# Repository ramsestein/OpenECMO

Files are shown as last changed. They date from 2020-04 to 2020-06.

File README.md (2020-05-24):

# ECMO

*Extra Corporeal Membrane Oxygenation* 

> *Nota:* Este documento se actualiza continuamente a medida que evoluciona el proyecto, por favor, revísalo frecuentemente y si crees que falta algo solicita que lo actualicemos.

## ¿Qué es una ECMO? ##
Una **ECMO** o **Membrana de Oxigenación Extra Corpórea** es una asistencia mecánica circulatoria y respiratoria, capaz de proporcionar soporte cardíaco y pulmonar, durante un periodo de días o semanas, para la insuficiencia cardiaca o respiratoria refractarias a tratamiento convencional. Es en resumen un soporte vital extracorpóreo con oxigenador incorporado. 

> A diferencia de los sistemas de perfusión o bypass cardio-pulmonar que están diseñados para sustituir de forma completa y breve la función del corazón y pulmón en el quirófano y así facilitar la cirugía, la **ECMO** mantiene la asistencia necesaria para garantizar las funciones vitales durante un periodo de tiempo mayor.

Este artículo de la _Revista Española de Perfusión_ nos parece muy interesante e ilustrativo para todos aquellos que quieran entender el problema y sería casi de lectura obligatoria si realmente quieres ayudar: [Soporte vital extracorpóreo. Oxigenación por
membrana extracorpórea. ECMO](https://www.aep.es/articulo/71/Monogra%CC%81fico%20ECMO.pdf "Soporte vital extracorpóreo. Oxigenación por
membrana extracorpórea. ECMO")

El dispositivo que queremos crear es del tipo ECMO V-V (Venoso-Venoso), que plantea menos problemas de presión sanguínea que el V-A (Venoso-Arteria)

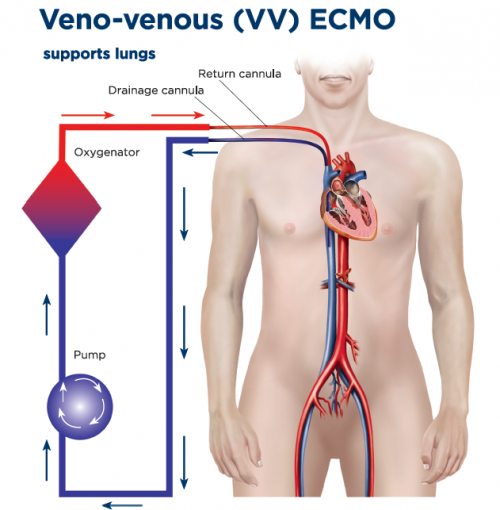
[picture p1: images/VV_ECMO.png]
ECMO Venoso-Venoso


## ¿Por qué un ECMO?

**El problema**
Además de la falta de respiradores hay otra crisis que inicialmente se pasó por alto: 
https://www.infobae.com/america/the-new-york-times/2020/04/19/coronavirus-ademas-de-la-falta-de-respiradores-hay-otra-crisis-que-se-paso-por-alto/

**¿Qué se puede hacer?**
Ramsés Marrero convova en el foro A.I.R.E. https://foro.coronavirusmakers.org/index.php?p=/discussion/comment/2749 este proyecto de clase 3.

## El proyecto ##
Intentamos construir una ECMO maker que cumpla con parámetros hemodinámicos suficientes para mantener con vida a pacientes muy graves afecados por COVID-19. 

> Recuerda que se trata de emular el comportamiento de un dispositivo comercial pero queremos construir algo low-cost pero con garantías médicas.

> *Nota importante:* Todos los que se acaben de añadir al proyecto les recomedamos la visualización del siguiente **[vídeo](https://gitlab.com/coronavirusmakers/ecmo/-/raw/master/files/zoom_Ramses.mp4?inline=true "Ramsés explica en que consiste un ECMO")** de una videoconferencia en la que el médico Ramsés Marrero explica de que se trata.
También rogamos encarecidamente que lean toda la información disponible antes de preguntar por los grupos de Telegram cuestiones que ya están resueltas.

Los objetivos hemodinámicos que debemos intentar conseguir tras la colocación del ECMO son:
* Flujo inicial del ECMO 50 – 80 ml/Kg./min. 
* Presión arterial media ≥ 65 mmHg. 
* Índice cardiaco ≥ 2.5 l/min./m2. 
* Presión de enclavamiento de arteria pulmonar (PEAP) 8-14 mmHg
* PVC 8-10 mmHg. 
* Saturación venosa mixta >65%. 
* Restauración de la diuresis (>0,5 ml/Kg. /h.) 
* Disminuir el ácido láctico en las primeras 4 horas.

## Esquema inicial ##

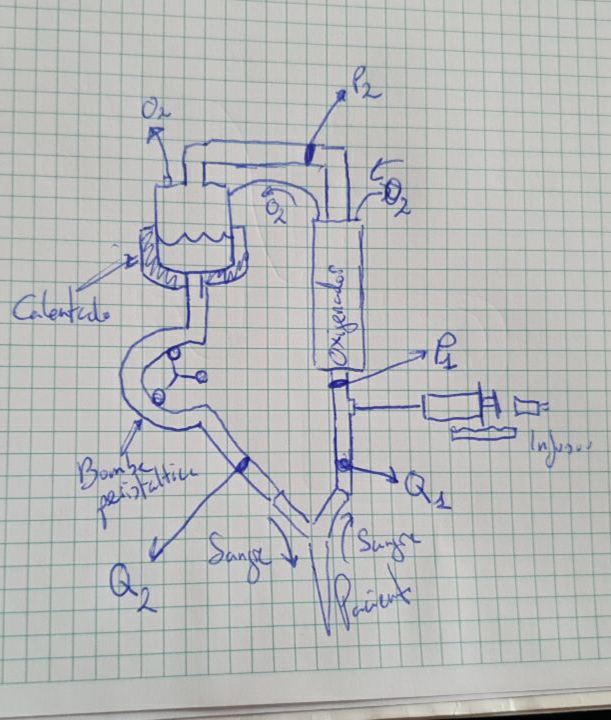
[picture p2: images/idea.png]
Idea Ramsés explica en que consiste un ECMO


*Presiones intrasistema:*
* P1: presión negativa de succión venosa (valores normales hasta -70 mmHg)
* P2: presión entre la bomba y el oxigenador (valor máximo de la normalidad entre   250 - 300 mmHg).
* P3: presión entre el oxigenador y la cánula arterial (valor máximo de la normalidad entre 250 – 300 mmHg).
* Diferencial de presión (calculado) ∆P (P2 – P3)

## Componentes del sistema ##

### Consola ###
* Es la encargada del control hemodinámico del sistema.
* Permite regular la velocidad de rotación de la bomba peristáltica (RPM) y el flujo en litros por minuto (LPM)
* Muestra la información aportada por los sensores hemodinámicos, bioquímicos o de seguridad implantados en el circuito.

### Bomba peristáltica ###
* Se necesita lograr un caudal de hasta 6 Litros por minuto (Lpm).
* Se descarta el uso de una bomba centrífuga porque tendría que ser de grado médico aunque es la que se usa en sistemas comerciales modernos.

### Tubos ###
* El tubo interior que aplasta debe tener un diámetro de 7mm externo y 6mm de diámetro interno para aprovechar los que hay de forma abundante en los hospitales.
* Para conseguir suficiente caudal (de hasta 6Lpm) se ha determinado que serán necesarios al menos dos tubos de ese diámetro.
* Los tubos no tienen porque ser de grado médico, podrían valer tubos de acuario suficientemente blando para poder aplastarse en la bomba peristáltica (* para los prototipos)

### Sensores ###

Algunas ideas:
* Interesa conocer la presión antes y después del filtro y también al final del recorrido
* De nuevo la presión hay que medirla de forma indirecta (sin “tocar” la sangre) o utilizar sensores desechables.

* Presión:
    * Dendrómetro
    * Webcam + machine learnnig para ver el flujo
    * Ultrasonidos / Doppler
    * Sensores barométricos / de presión
    * Detectar el desplazamiento de una jeringuilla de baja presión
    
* Para detectar obstruccion:
    * Utilización de un oxímetro
    * Medida de la corriente del motor o uso de sensores hall para determinar si la velocidad de giro es la prefijada.

### Oxigenador ###
Es el elemento esencial del EMCO, la membrana que permite la oxigenación de la sangre del paciente. 
* Opción de usar un modelo comercial.
* Se están estudiando tamnbién distintas opciones de fabricación 

### Perfusor ###
Es un elemento adicional (independiente) que permite la infusión de heparina para evitar la coagulación de la sangre.

## Colaboración ##

Si crees que puedes ayudar entra en los grupos de Telegram y dirígete al subgrupo en el que creas que puedes aportar más: 
https://t.me/joinchat/AEZqrlHdWOAwDOvL7WSOKA

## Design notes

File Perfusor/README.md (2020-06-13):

# Perfusor #

## Descripción ##
La bomba de perfusion (o infusión) es un dispositivo que dispensa fluido durante un período de tiempo determinado. 

Info de la wikipedia: https://es.wikipedia.org/wiki/Bomba_de_infusi%C3%B3n

## Proyecto ##
* El diseño mecánico se basa en un diseño de actuador lineal junto a una jeringa, controlado por un sistema electrónico.
* El dispositivo debe ser independiente del resto del sistema [ECMO](https://gitlab.com/coronavirusmakers/ecmo "ECMO").
* La jeringa se coloca en el perfusor ya purgada.

El diseño usara una jeringa 50-60 ml tipo BD Plastic o similar (diametro 26.7 mm) 

[Jeringuilla](https://gitlab.com/coronavirusmakers/ecmo/-/raw/master/images/jeringuilla.jpeg "Jeringuilla de 50-60ml")

[Datos y tamaños de las jeringuillas](https://gitlab.com/coronavirusmakers/ecmo/-/raw/master/files/Syringe-Selection-Guide.pdf "Datos de las jeringuillas")

## Requerimientos funcionales ##
* Tenemos que lograr un control entre 0.1ml/h - 1200ml/h para una jeringuilla de 50ml (valores calculados)
* Resolución de 0.1 mL
* Dosis tipica es de 2-15ml/h
* Velocidad ajustable
* Posibilidad de hacer una embolada puntual de x mL
* Indicación de estado
* indicador de alarma cuando este al 95% del final
*  La interface de usuario debe permitir:
    * Indicar y modificar la velocidad de perfusion
    * Cargar nueva jeringa (volver al inicio de carrera)

## Hardware ##

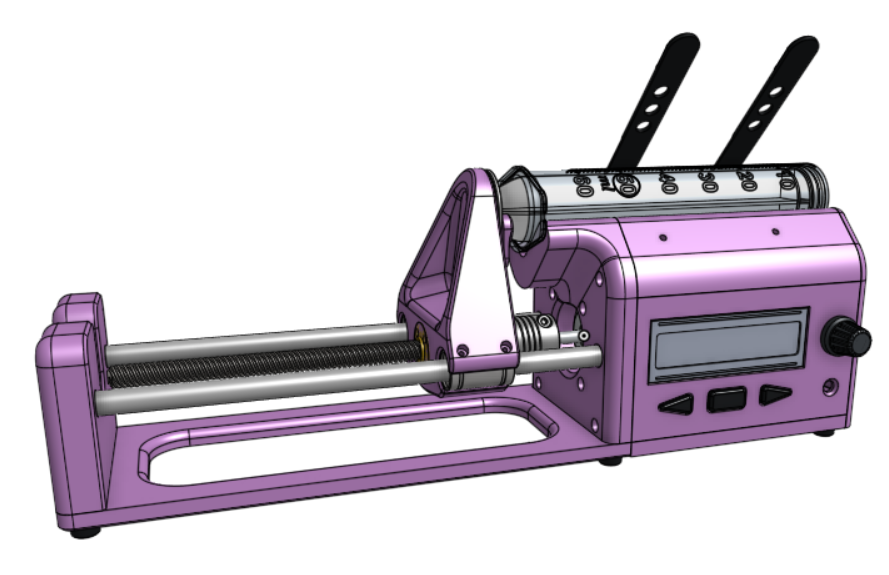
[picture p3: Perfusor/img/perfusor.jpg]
Montaje del perfusor


### Mecánica ###

El sitema mecánico consta de:
* Piezas impresas en 3D
* Motor paso a paso nema 17
* Un sistema de husillo / cremallera.. (por concretar)
* 2 Rodamientos LM8UU
* Tornillos M3

### Electrónica ###
El sitema electrónico consta de:
* 1 Fuente de alimentación de 12V
* 1 Conversor DC-DC
* 1 microcontrolador tipo Arduino o un microprocesador similar
*  Motor diver supported by [AccelStepper](https://www.airspayce.com/mikem/arduino/AccelStepper/index.html)
* 1 sensor final de carrera o endstop (mejor óptico o hall para evitar problemas de pérdida de pasos pero también pueden ser mecánicos)
* Display (Pantalla LCD I2C 16x2, 20x4 u OLED)
* Tres botones
* Codificador rotatorio (encoder para selección de opciones) o un potenciómetro
* LEDs indicadores de estado (Verde: Operativo; Rojo: Alarma)
* Alarma sonora (zumbador) 

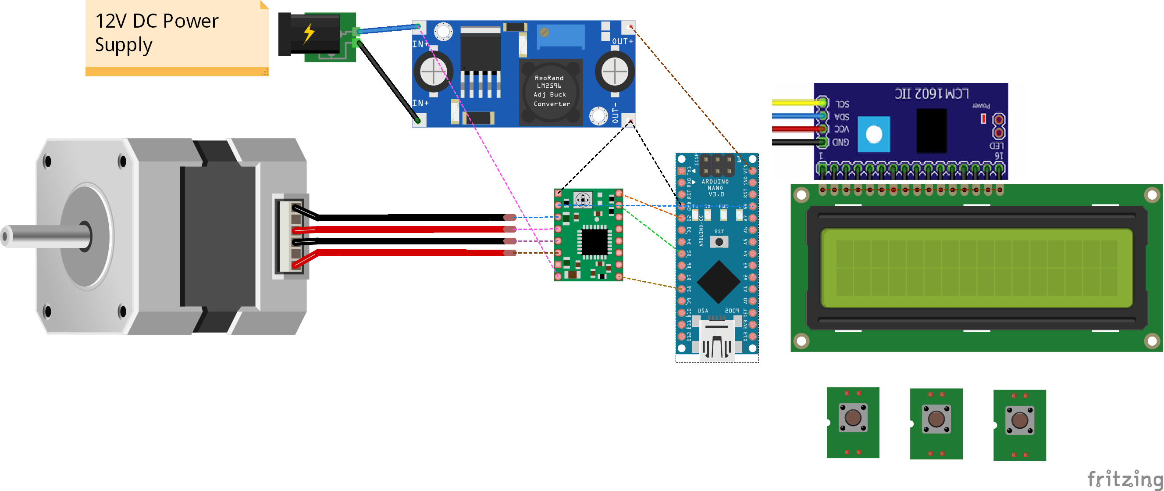
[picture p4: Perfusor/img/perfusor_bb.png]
Esquema del perfusor

(Este esquema está incompleto pero sirve como referencia)
## Diseño actual (en desarollo) ##

https://cad.onshape.com/documents/83fc61005005f6cafa1e611e/w/66630729656df7a5a0b484c3/e/114f94c28aaf946ab67668a8

En la carpeta stl hay unos archivos en formato .stl para la  impresión en 3D de la estructura del dispositivo.

https://gitlab.com/coronavirusmakers/ecmo/-/tree/master/Perfusor/stl 

En la carpeta stl/Plastikete hay una versión low-cost completamente de plástico

https://gitlab.com/coronavirusmakers/ecmo/-/tree/master/Perfusor/stl/Plastikete 

## Como testear el perfusor

## Enlaces de interes ##
### Diseños ###
1. http://biohackacademy.github.io/biofactory/class/8-pumps/
2. https://github.com/gniezen/openpump
3. https://docs.google.com/document/d/1zW16lL-d0ZAO8lZd7ANE9CllARVIuFvh3bQfag9HGlk/mobilebasic#

### Cálculos ###

    * Aquí tenemos un enlace con cálculos al respecto de los husillos: https://docs.google.com/spreadsheets/d/1-_jbQUJL_gpxpd1H1qJIKm36sRTwBJtxHg9JuVWixjs/edit#gid=0

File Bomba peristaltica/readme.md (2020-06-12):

# Bomba Peristáltica  #

## Descripción ##
Una bomba peristáltica es un tipo de bomba hidráulica de desplazamiento positivo usada para bombear una variedad de fluidos.
Nosotros queremos construir una bomba peristáltica para impulsar la sangre a través de un sistema venoso-venoso de un ECMO.

En el siguiente enlace https://ocw.unican.es/mod/page/view.php?id=537 hay una sencilla pero completa descripción de la hemodinámica o física del flujo sanguíneo.

## Requerimientos funcionales ##
* Bombeo continuo
* Resolución de 1 ml
* Dirección hacia adelante / hacia atrás
* Velocidad ajustable

## Hardware ##

El sitema *mecánico* consta de:
* Motor paso a paso
* Una caja impresa en 3D con rodamientos para hacer la bomba peristáltica 
* Tubos para diálisis de 6mm de diámetro interior y 7mm de diámetro exterior

El sitema *electrónico* consta de:
* Arduino Nano o similar
* Driver para el motor
* Motor paso a paso Nema 23 con eje de 6.35 u 8 mm
* Display (Pantalla LCD I2C 16x2 u OLED)
* Codificador rotatorio (encoder)
* Un botón pera realizar emboladas rápidas. 
* (Quizá un segundo botón)
* LEDs indicadores de estado (Verde: Operativo; Rojo: Alarma)
* Zumbador de alarma

## Diseño actual (en desarollo) ##
Se han subido los archivos de un diseño 3D para motores nema 23 con ejes de 6,23 y 8mm en la carpeta STL que utiliza para probar rodamientos 608zz y otro modelo de bomba peristáltica llamada LEGO.

Estas son algunas imágenes del modelo LEGO:

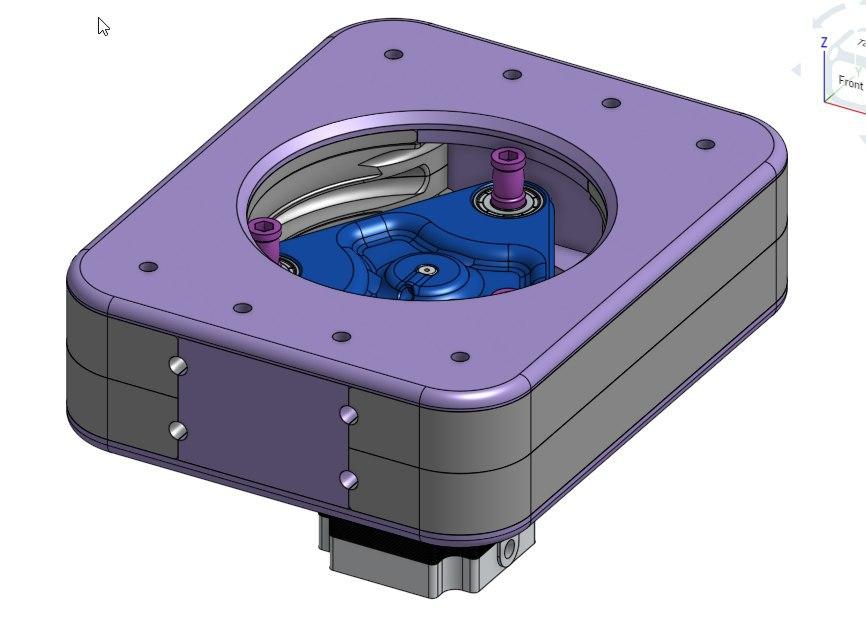
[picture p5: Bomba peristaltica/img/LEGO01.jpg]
LEGO01


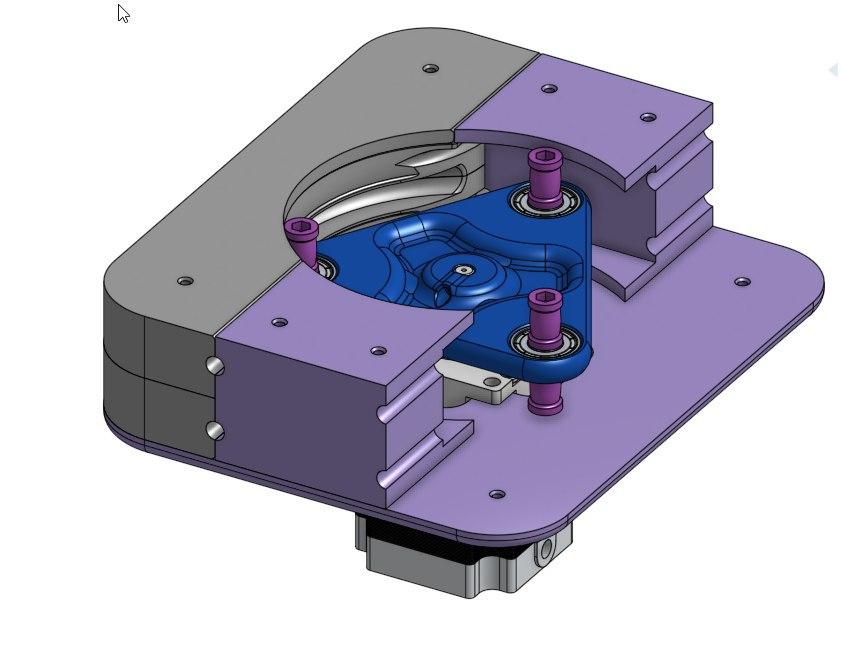
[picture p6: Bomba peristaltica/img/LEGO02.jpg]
LEGO02


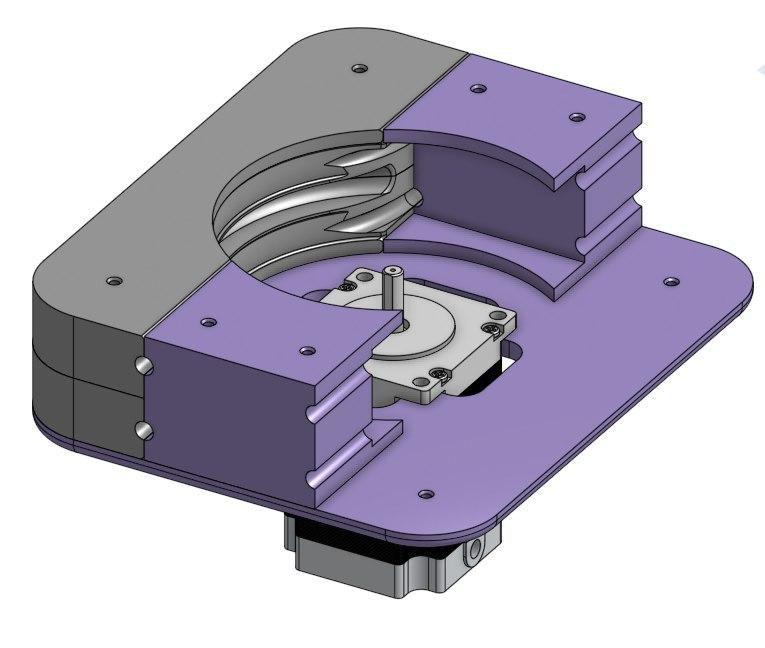
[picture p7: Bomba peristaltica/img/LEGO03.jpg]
LEGO03


Deben utilizarse tubos de 7mm de diámetros exterior y 6mm de diámetro exterior habituales en los hospitales y que se utilizan para diálisis.

## Como testear el bomba persitaltica
* Medición de consumo de corriente
* Encoder
* Sensor hall 

## Enlaces de interes ##
### Diseños ###
1. http://biohackacademy.github.io/biofactory/class/8-pumps/
2. http://2017.igem.org/Team:Aachen/Hardware

### Cálculos ###
1. https://leadfluid.com/how-to-calculate-the-flow-rate-of-leadfluid-peristaltic-pump/

### Médico ###
1. https://ocw.unican.es/mod/page/view.php?id=537

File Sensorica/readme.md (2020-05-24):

**Objetivo**

El objetivo del Sistema de sensores es medir la presión/caudal del sistema y la saturación de oxigeno

**Requisitos**

1. No se puede acceder al líquido, es decir, los sensores no pueden estar en contacto con el líquido y ese es el gran problema
2. Sencillo, barato y fácil de construir.

**Técnicas**

Se ha pensado en las siguientes técnicas:

1. Medida de presión dendrométrica, presionando el tubo y ver la resistencia que ofrece
2. Medida de la velocidad del líquido mediante un sistema óptico o ultrasónico.
3. Medida de O2 en sangre mediante sistema óptico (Colorimetria).

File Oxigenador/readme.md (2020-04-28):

# Intercambiador gases

## Descripción

## Tipos

### PMP

### PDMS

## Como testear el intercambiador de gases

Agitador magnetico

Bomba persitaltica

Sensor presión

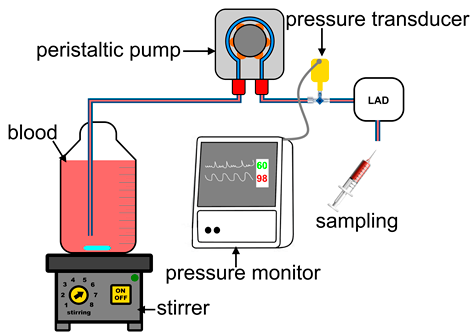
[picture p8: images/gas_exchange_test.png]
Diagrama test intercambiador gas


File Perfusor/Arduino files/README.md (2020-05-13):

# Perfusor
## Overview
The goal is to develop **firmware based on arduino for an syringe driver (infusion pump)**, used to gradually administer small amounts of fluid to a patient, in this case, heparin.
## Hardware Requirements
* Microcontroller: Arduino (any version) or similar 
*  Motor diver supported by [AccelStepper](https://www.airspayce.com/mikem/arduino/AccelStepper/index.html)
* 3 Buttons 
* End stop 
* LCD Display 
* Potentiometer
* Syringe support
* Incremental Encoder(optical+disc)

## How to use it
1. Clone the repository
1. Set up the code in the src/Configuration.h file:
   1. Configure your display
      1. Number of rows
      1. Number of cols
      1. I2C Address of the device
   1. Configure the syringe driver: 
      1. Slider length in mm
      1. Number of steps per turn   
      1. How much it moves per turn
   1. Choose your stepper dirver NEMA17 or BJY. If you want to use any other you have to take into account the interface that it requires and the pins needed.
  *Note: If you are using inverted pins for the driver changes need to be made in the constructor of SyringeDriver (SyringeDriver::SyringeDriver())*
   1. Change the pinout if needed.
1. **Compile and upload the code!**

## Libraries 
* [AccelStepper](https://www.airspayce.com/mikem/arduino/AccelStepper/index.html)
* [NewLiquidCrystal](https://bitbucket.org/fmalpartida/new-liquidcrystal/wiki/Home#!tests)

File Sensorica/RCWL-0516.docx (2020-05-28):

SENSOR DOPPLER MICROONDAS RCWL-0516

1. INTRODUCCIÓN

Para la medida de velocidad de fluidos se ha elegido el módulo RCWL-0516. Este módulo es un interruptor de detección por microondas, que utiliza la frecuencia Doppler de detección. Como utiliza frecuencia Doppler, el circuito no detecta la presencia de un objeto estático delante del sensor, sino el movimiento (velocidad) de un objeto delante del sensor. Al tratarse de un interruptor no es posible utilizar directamente la señal de salida del detector para medir la velocidad.

2. DOCUMENTACION
a) https://www.rogerclark.net/investigating-a-rcwl-9196-rcwl-0516-radar-motion-detector-modules/
b) https://www.tayloredge.com/reference/Electronics/RF/0242.pdf
3. MEDIDA DE VELOCIDAD

Para medir la velocidad de un móvil delante del sensor es preciso acceder a la medida de la frecuencia Doppler. Para ello es preciso extraer la tensión diferencial en la etapa de amplificación del circuito detector (pin 12 del IC RCWL-9196).

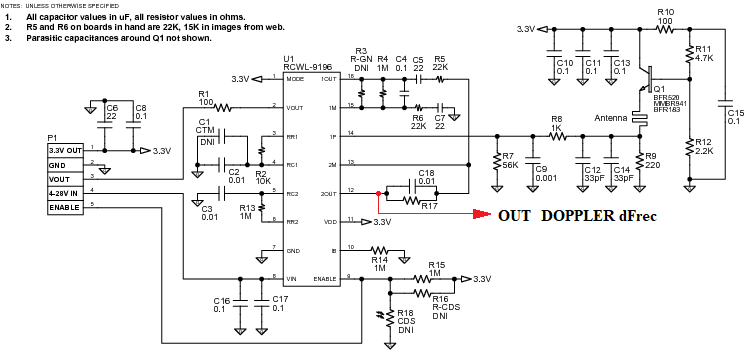
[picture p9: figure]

Fig 1

4. ESTUDIO DEL UMBRAL DE VELOCIDAD DETECTABLE

La señal 2Out del pin 12 del IC RCWL-9196 es una señal analógica cuyo nivel dependerá de la frecuencia de oscilación del circuito resonante conectado en el pin 14 (1C).

VM = Vref * 0.5

Para FDoppler = Frecuencia central tenemos que Vout (2Out) = VM

Si Vref = 5V, luego VM = 2.5V.

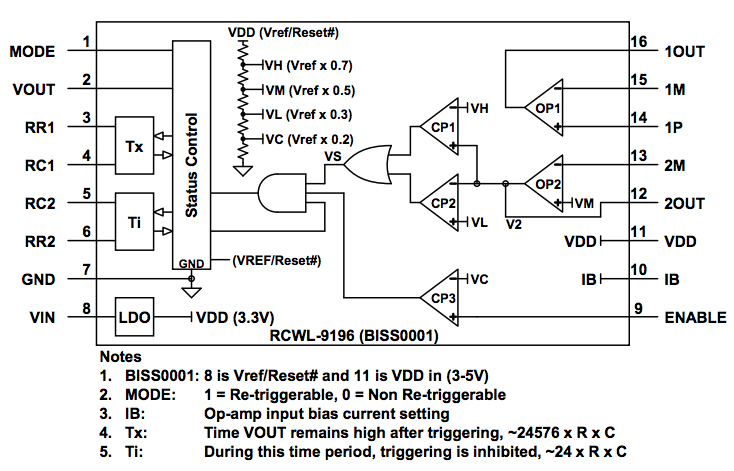
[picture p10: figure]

Fig 2

VL y VH limitan el rango dinámico que para Vref = 5V son VL = 1.5V y VH = 3.5V. El rango dinámico delimita el umbral de la velocidad detectable.

5. APLICABILIDAD A LA MEDIDA DE VELOCIDAD EN UN FLUIDO

La detección de la velocidad de un fluido en movimiento se realiza mediante la medida Doppler sobre las propias moléculas del fluido en movimiento.

6. PRUEBAS CON CORRIENTE DE AGUA

Ejecución de la prueba: Colocando el sensor a 20cm de un grifo abierto el sensor detecta el agua circulando.

Código de prueba:

const int LEDPin = 13;

const int RadarPin = 2;

void setup()

{

pinMode(LEDPin, OUTPUT);

pinMode(RadarPin, INPUT);

pinMode(A0,INPUT);

Serial.begin(9600);

}

void loop()

{

int value= digitalRead(RadarPin);

medida = 0;

if (value == HIGH)

{

digitalWrite(LEDPin, HIGH);

delay(50);

digitalWrite(LEDPin, LOW);

delay(50);

}

else

{

digitalWrite(LEDPin, LOW);

}

}

7. DETECCION DE VELOCIDAD

Para detectar la velocidad de movimiento de un objeto delante del sensor se utiliza el esquema de la figura 1. La tensión en el pin 12 del IC es un valor de tensión analógico entre 0 y Vcc (5V si se conecta a Arduino). Este valor queda limitado a l umbral entre VL y VH. La tensión se acopla a una entrada analógica (A0) del Arduino.

Durante la prueba se comprobado que incluso sin conectar el cable al pin 12 se ha producido inducción en el cable detectando cambios de nivel en función del movimiento delante del sensor.

Código de prueba:

const int LEDPin = 13;

const int RadarPin = 2;

float medida = 0.0;

void setup()

{

pinMode(LEDPin, OUTPUT);

pinMode(RadarPin, INPUT);

pinMode(A0,INPUT);

Serial.begin(9600);

}

void loop()

{

int value= digitalRead(RadarPin);

medida = 0;

if (value == HIGH)

{

digitalWrite(LEDPin, HIGH);

delay(50);

digitalWrite(LEDPin, LOW);

delay(50);

}

else

{

digitalWrite(LEDPin, LOW);

}

for (int i = 0; i <= 100; i++) {

medida = medida + analogRead(Speed);

}

medida = medida / 100;

Serial.println(medida-20);

}

Imágenes:

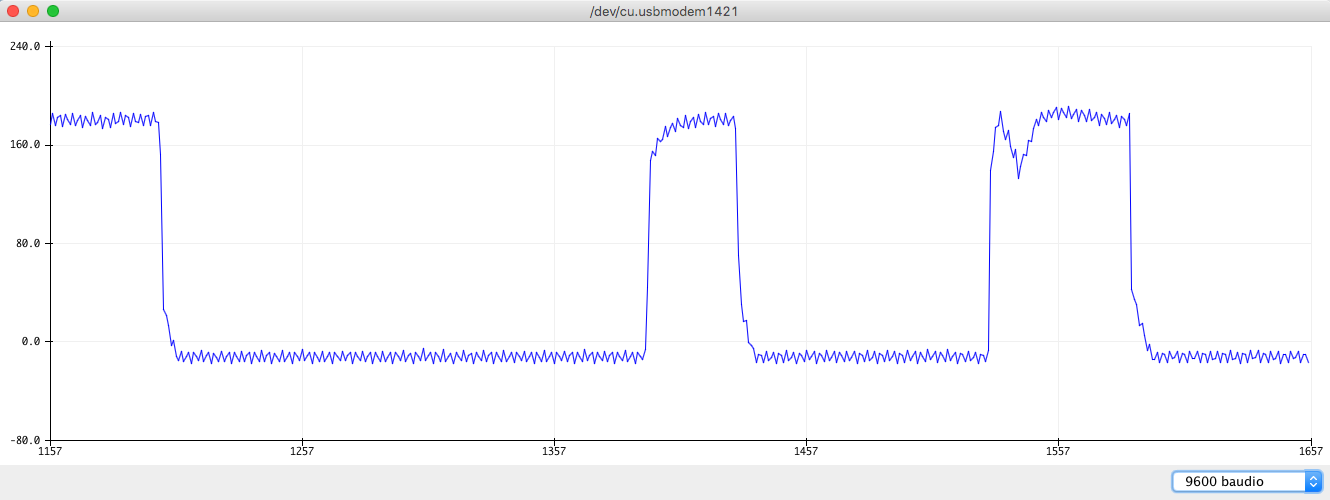
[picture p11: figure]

Fig 3

8. CONCLUSIONES:
- El sensor RCWL-0516 está pensado para la detección de movimiento, no la medida del movimiento.
- Sin embargo, se podría medir el movimiento detectado tomando la tensión del pin descrito.
- La medida de movimiento puede ser ruidosa si no se aisla convenientemente el sensor.

Francisco José Ochando Terreros

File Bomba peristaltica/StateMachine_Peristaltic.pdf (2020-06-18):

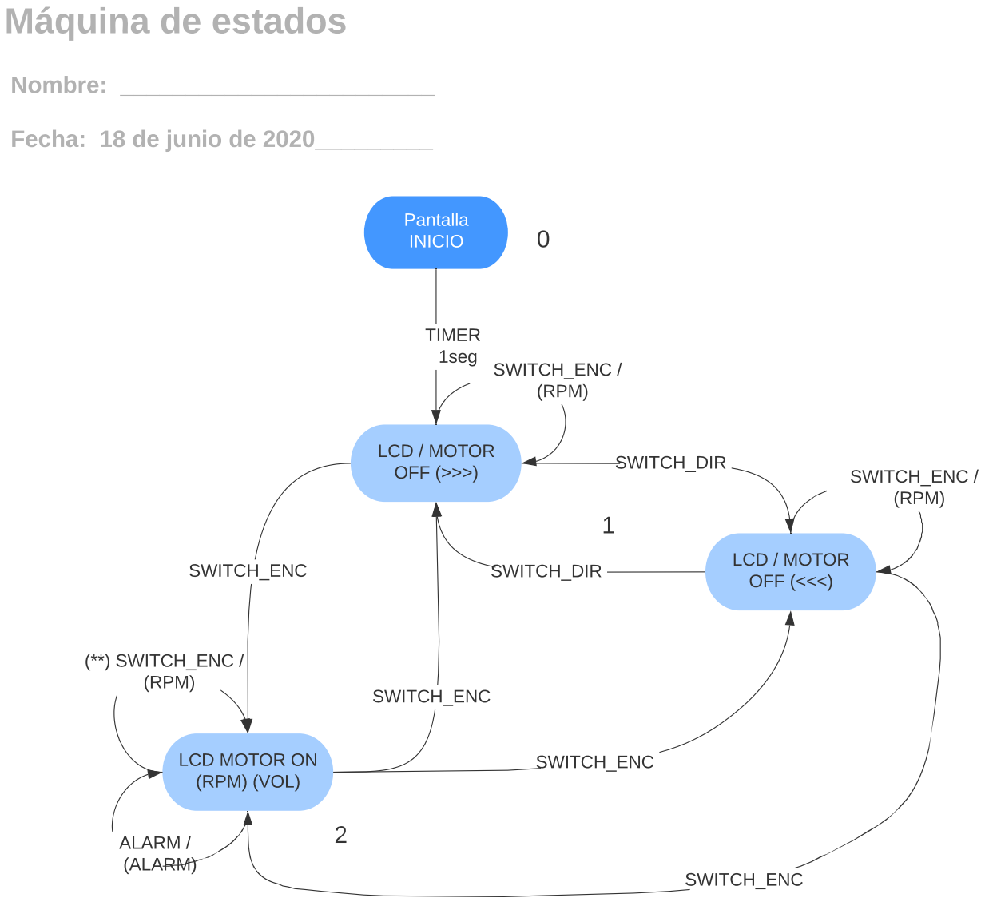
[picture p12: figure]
Pantalla INICIO; LCD MOTOR ON (RPM) (VOL); Máquina de estados; Nombre: ________________________; Fecha: 18 de junio de 2020_________; SWITCH_ENC; LCD / MOTOR OFF (>>>); TIMER 1seg; LCD / MOTOR OFF (<<<); SWITCH_DIR; SWITCH_ENC / (RPM); ALARM / (ALARM); (**) SWITCH_ENC / (RPM)

(0) La Pantalla 0 muestra la información en la pantalla de bienvenida.
(1) La pantalla 1 muestra toda la información (por defecto si no se ha programado una velocidad distinta)
(2) La pantalla 2 muestra toda la información más <ON> y <ALARM> si existe alguna alarma. Motor activado.
(**) El evento mover el potenciometro/encoder rotativo durante el funcionamiento del motor varia los parámetros de giro del motor durante el funcionamiento. Hay que revisar este requisito.

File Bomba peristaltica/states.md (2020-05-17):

# Estados de la máquina

## Documento que describe los estados de la Máquina
En el presente documento se describen los estados de la máquina del LCD en función del estado de los botones, el encoder y los sensores.
El LCD utilizado es un 20x4. La configuración para un LCD 16x2 es posible.
Simulación de LCD en: http://avtanski.net/projects/lcd/

## Estados del LCD en función de los estados de la Máquina
1.	Estado de arranque
Al arrancar la máquina muestra la presentación de bienvenida y las RPM por defecto (configuración de inicio a determinar).

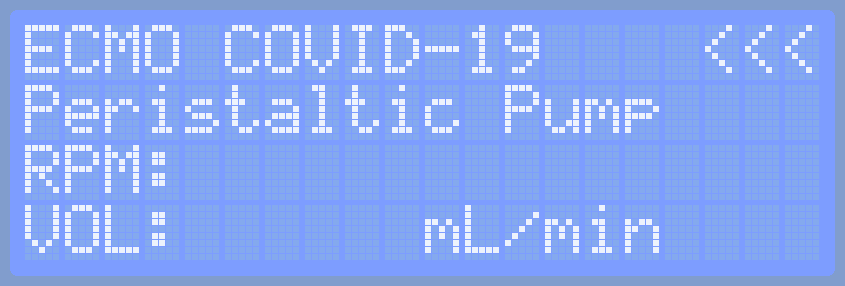
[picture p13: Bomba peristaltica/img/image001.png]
Pantalla inicial del LCD de la bomba peristáltica


2.	Estado de configuración inicio
	Al pulsar el SWITCH_REV se invierte el sentido de la bomba. Esto sólo es posi-ble antes de la marcha del motor o una vez detenido. 

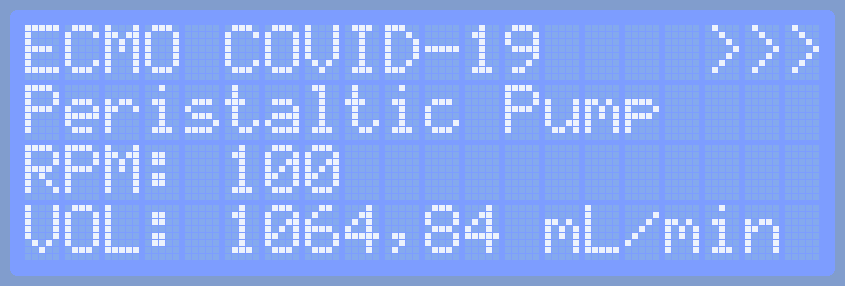
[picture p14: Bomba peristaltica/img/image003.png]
Invirtiendo el sentido de giro


3.	Estado de selección de RPM
	La selección de RPM es posible en el modo de configuración inicial o durante el modo de funcionamiento actuando sobre el ENCODER ROTATIVO (varian las RPM y el caudal - VOL).

Selección de RPM

4.	Estado de funcionamiento
	Al pulsar SWITCH_ENC se arranca la bomba con la velocidad configurada (ON). Así mismo, al pulsar el mismo, se para la bomba.

5.	Estado de Alarma (funcionamiento)
	Durante el funcionamiento la pantalla LCD muestra el estado <ALARM> si re-produce un desajuste de las RPM por causa de un bloqueo del Sistema.
 
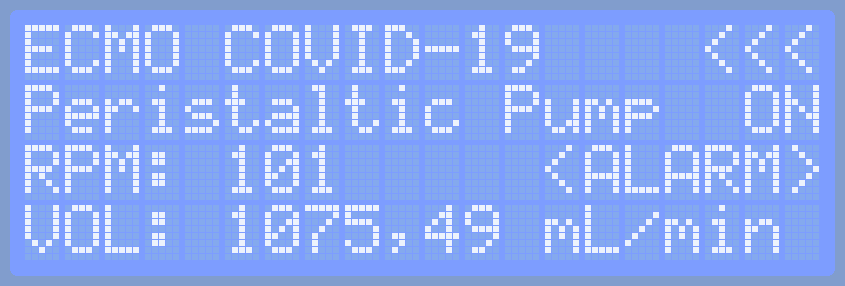
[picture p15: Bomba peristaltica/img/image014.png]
Estado de Alarma


6.	Estado de OFF

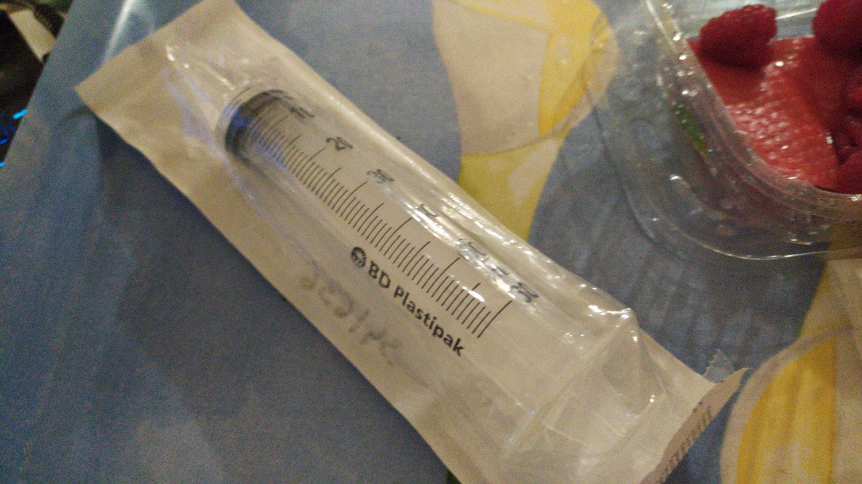
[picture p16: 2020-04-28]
images/jeringuilla.jpeg

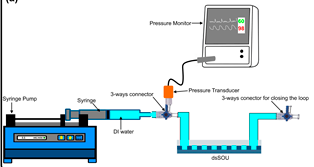
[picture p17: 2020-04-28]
images/burst_pressure.png

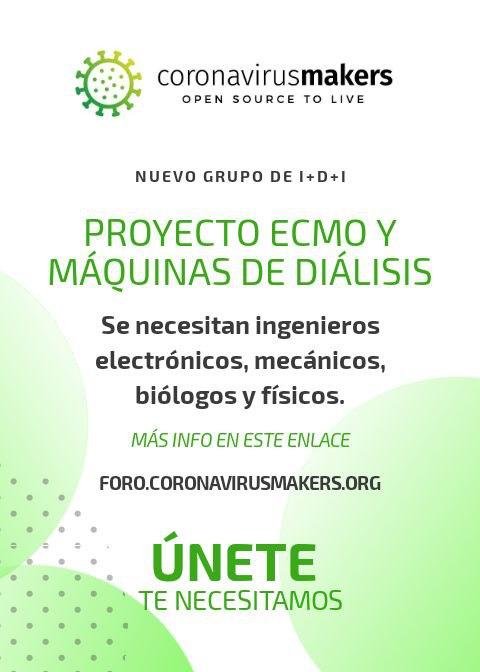
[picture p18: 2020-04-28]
images/Grupo_I+D+i_ECMO.jpg

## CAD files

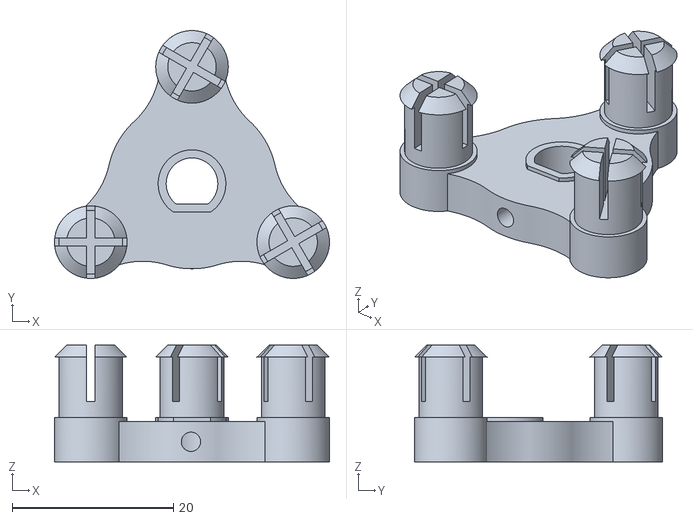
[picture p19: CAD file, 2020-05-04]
Bomba peristaltica/stl/6.35mm/Rotor.stl
34.1 x 30.7 x 14.5

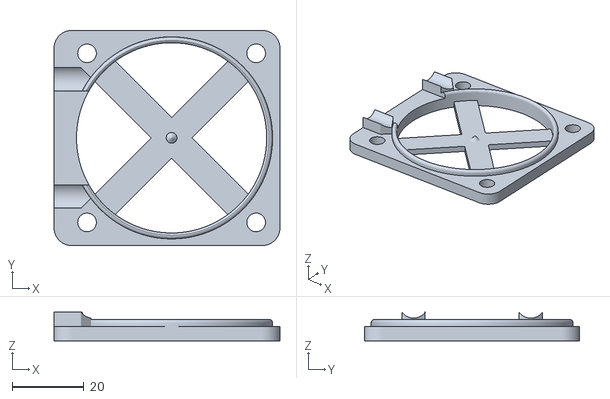
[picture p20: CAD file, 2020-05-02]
Bomba peristaltica/stl/8mm/Tapa8mm.stl
63.0 x 60.0 x 8.00

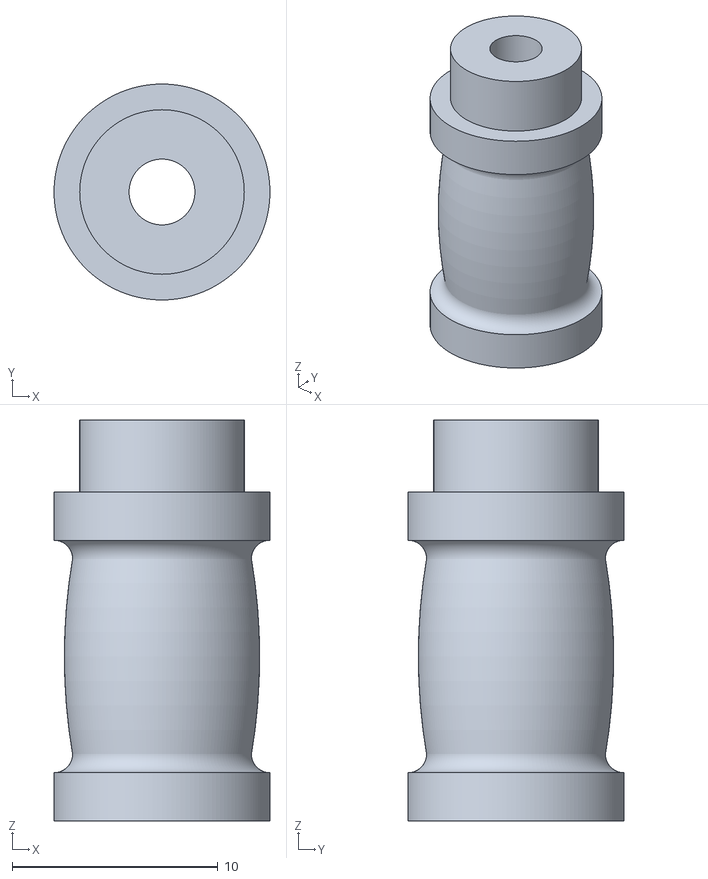
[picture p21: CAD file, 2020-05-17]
Bomba peristaltica/stl/LEGO/Rodillo superior.stl
10.5 x 10.5 x 19.5

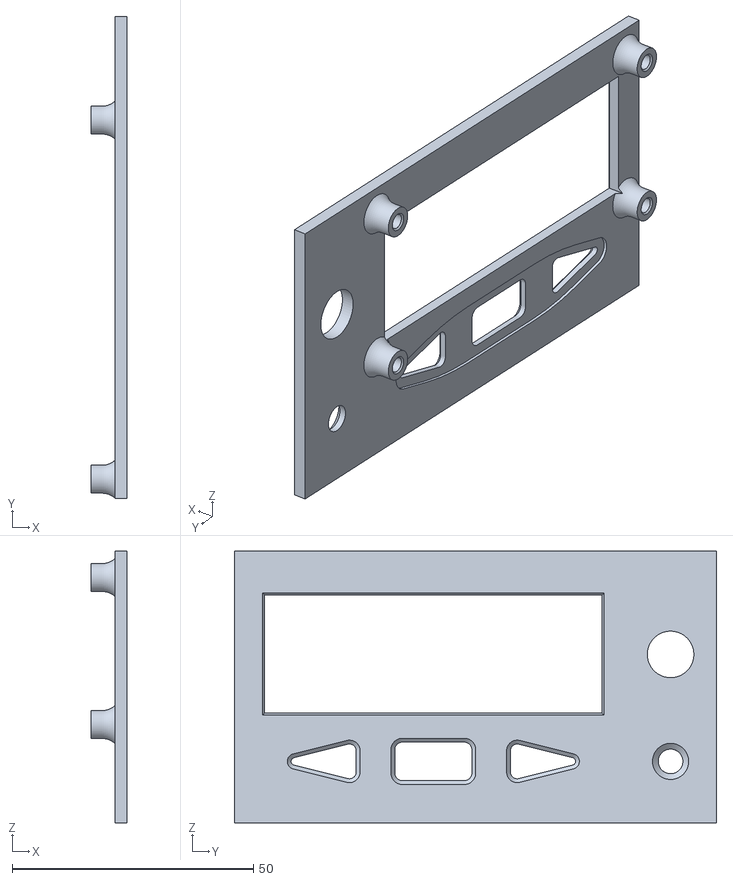
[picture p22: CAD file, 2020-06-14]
Perfusor/stl/Part Studio 11.stl
7.42 x 100.0 x 56.4

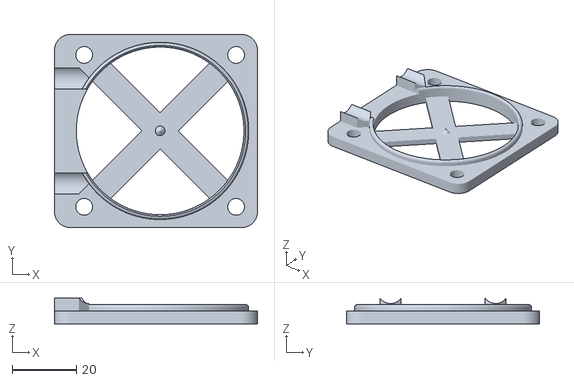
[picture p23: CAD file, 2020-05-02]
Bomba peristaltica/stl/6.35mm/Tapa.stl
63.0 x 60.0 x 8.00

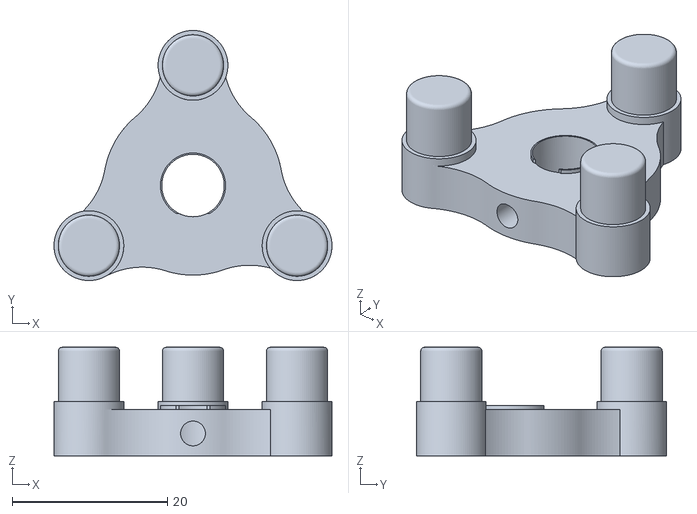
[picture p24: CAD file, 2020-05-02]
Bomba peristaltica/stl/8mm/Rotor8mm.stl
35.8 x 32.2 x 14.0

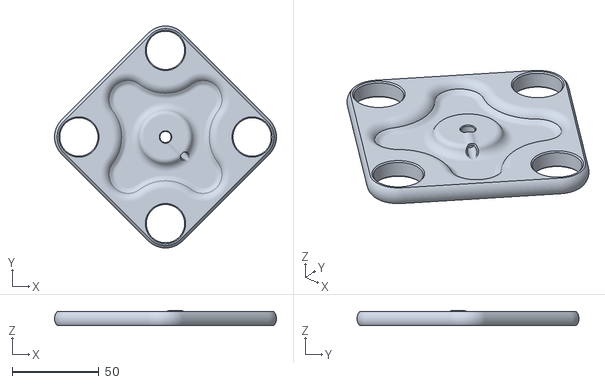
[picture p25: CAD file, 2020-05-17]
Bomba peristaltica/stl/LEGO/Rotor 4.stl
127.9 x 127.9 x 8.70

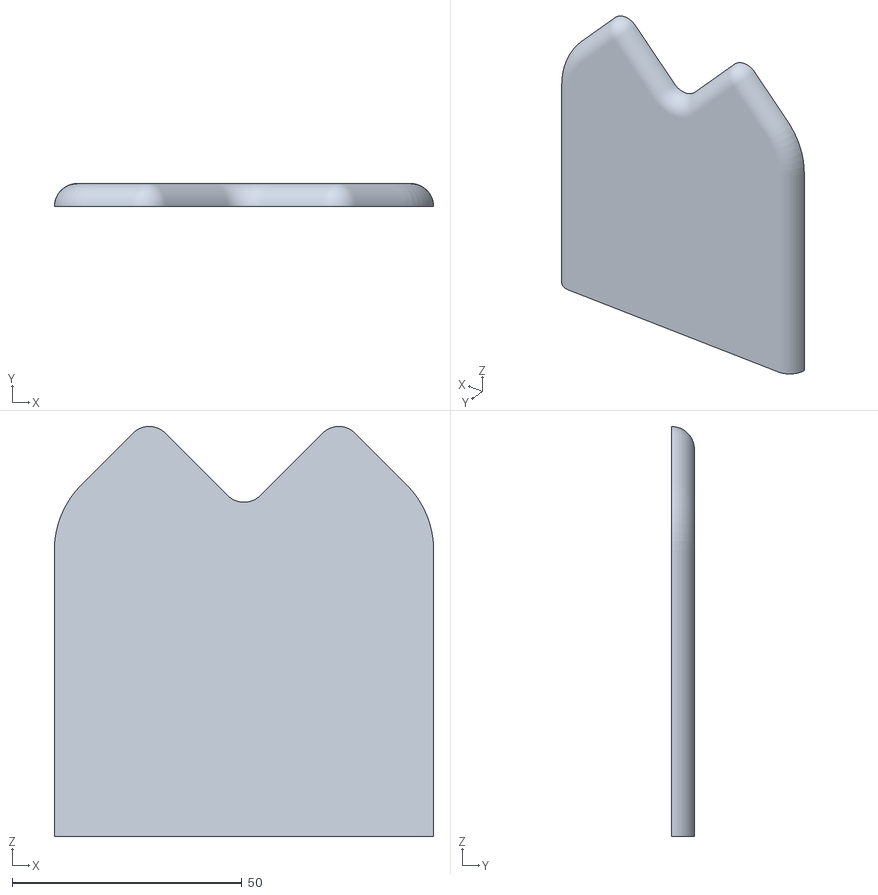
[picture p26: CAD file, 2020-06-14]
Perfusor/stl/Part Studio 12.stl
82.6 x 5.00 x 89.3

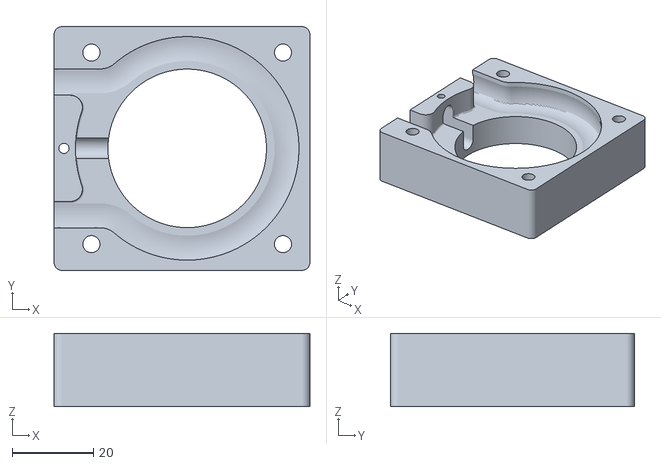
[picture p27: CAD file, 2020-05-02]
Bomba peristaltica/stl/6.35mm/Caja.stl
63.0 x 60.0 x 18.0

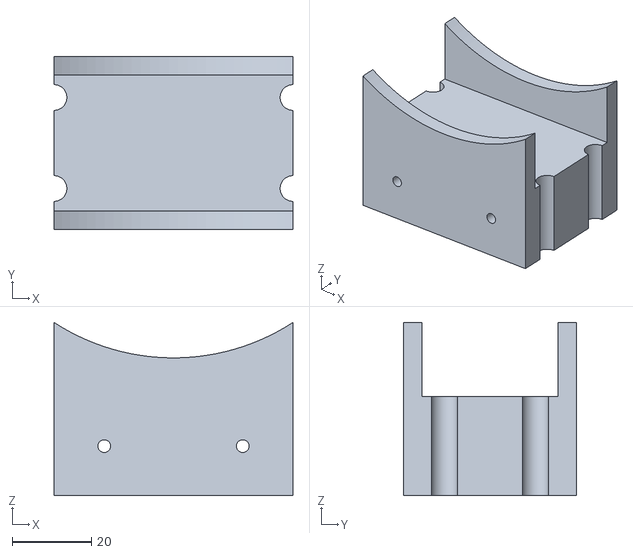
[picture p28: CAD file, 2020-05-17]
Bomba peristaltica/stl/LEGO/Lateral (x2).stl
60.4 x 43.6 x 43.8

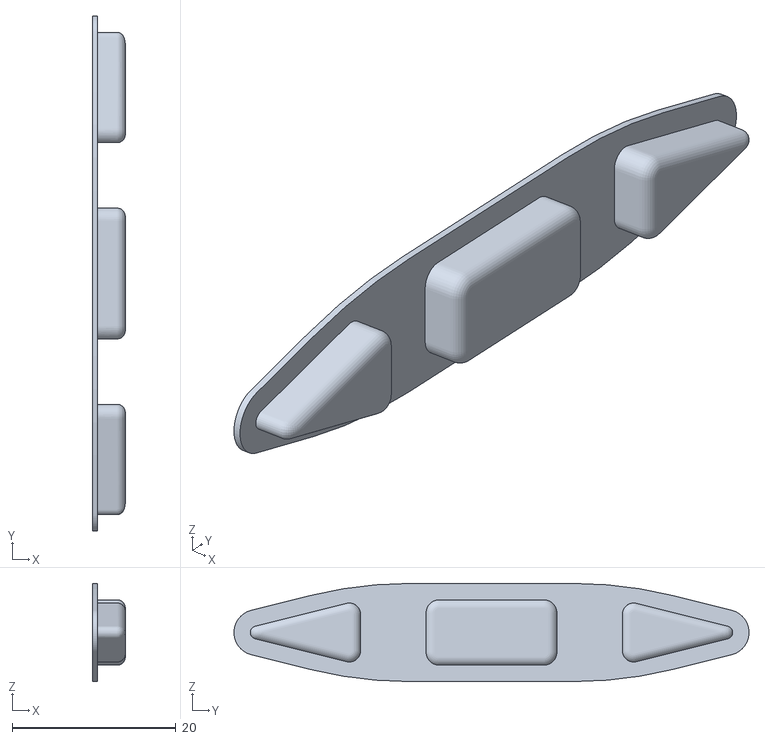
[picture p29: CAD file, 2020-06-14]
Perfusor/stl/Part Studio 13.stl
4.00 x 63.0 x 12.0

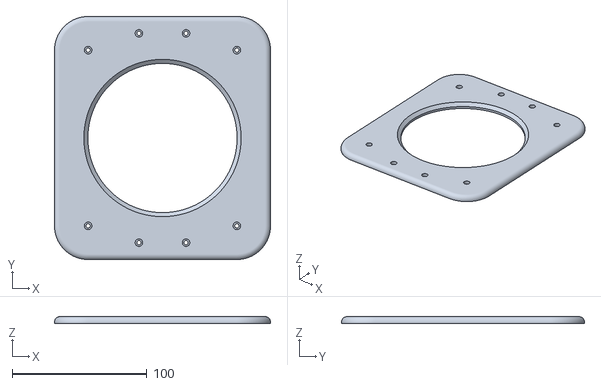
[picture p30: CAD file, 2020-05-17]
Bomba peristaltica/stl/LEGO/Tapa superior.stl
160.3 x 180.3 x 5.00

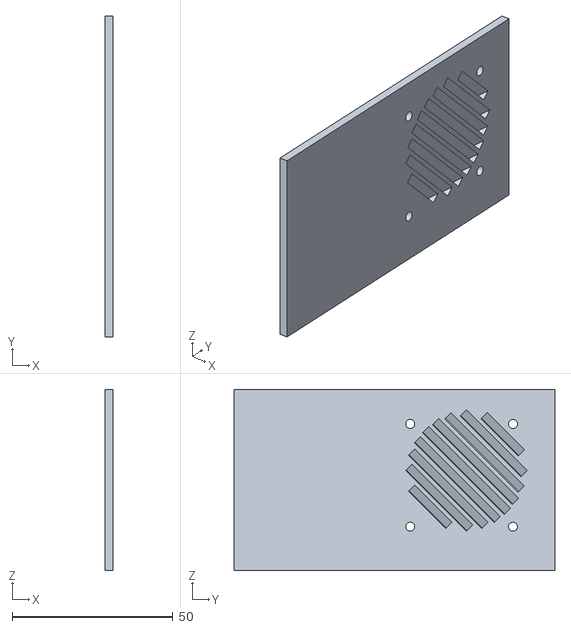
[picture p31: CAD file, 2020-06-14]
Perfusor/stl/Part Studio 9.stl
2.50 x 100.0 x 56.4

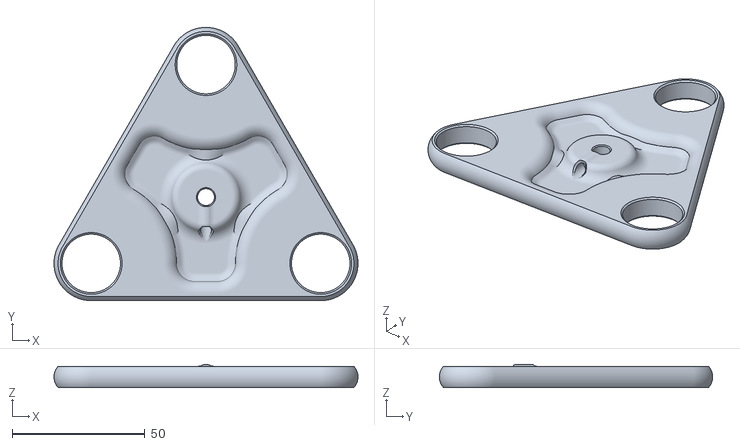
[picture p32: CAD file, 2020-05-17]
Bomba peristaltica/stl/LEGO/Rotor 3.stl
114.5 x 102.9 x 8.70

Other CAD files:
Bomba peristaltica/stl/8mm/Caja8mm.stl
Perfusor/stl/Part Studio 8.stl
Bomba peristaltica/stl/LEGO/Frontal (x4).stl
Perfusor/stl/Part Studio 10.stl
Bomba peristaltica/stl/LEGO/Rodillo inferior.stl
Bomba peristaltica/stl/LEGO/Tapa inferior.stl
Perfusor/stl/Part Studio 1.stl
Perfusor/stl/Part Studio 2.stl
Perfusor/stl/Part Studio 3.stl
Perfusor/stl/Part Studio 4.stl
Perfusor/stl/Part Studio 5.stl
Perfusor/stl/Part Studio 6.stl
Perfusor/stl/Part Studio 7.stl

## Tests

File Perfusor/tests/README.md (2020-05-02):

# Test
Carpeta de códigos de prueba del perfusor
* La subcarpeta LcdMenu es para probar el interfaz LCD por I2C o paralelo y los menús

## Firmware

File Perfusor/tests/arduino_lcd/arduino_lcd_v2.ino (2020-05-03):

/*
 * Perfusor EMCO
 * Basado en un LCD Menú de Mark Van Veggel
 * Licencia GPLv3
 */

#include <OneButton.h>
#include <Encoder.h>
#include <Wire.h>
#include <LCD.h>
#include <LiquidCrystal_I2C.h>

// LCD Display
LiquidCrystal_I2C  lcd(0x3F,2,1,0,4,5,6,7);

// ROTARY ENCODER
long oldPosition  = 0;
int encoderDTpin = 2;
int encoderCLKpin = 3;
Encoder myEnc(encoderDTpin, encoderCLKpin);
int buttonPin = 8;
OneButton button0(buttonPin, true);

// MENU ARRAY 
// First number in array = amount of menu items in root layer. Same goes for next layer. (Example: first value in array is 4. This means Layer 0 has 4 menu items. Layer 1 has only 2 menu items.)
// First number infront of menu text is the layer number that item points to. (Example: 1_Rotation points to Layer 1)
// Second number infront of menu text is the number of the value connected to that menu item in the values array. (Example: 15Direction points to position 5 in the values array)
// Primer nº del array = cantidad de items del menú en la capa raíz. Lo mismo para la sisguiente capa. (Ej.: si el primer valor del array es 4 significa que la Capa 0 tiene 4 items.
// El primer nº delante del texto de un menú es el nº de la capa a la que apunta. (Ej.: 1_Rotation apunta a la capa 1)
// El segundo nº delante del texto de un menú es el nº de la variable conectada a este item de menú en el array de valores. (Ej.: 15Direction apunta a la posición 5 en el array.

String menu[] = {"3","1__Iniciar perfus.","2__Config. perfus.","5__Sel. idioma",                                                          // Layer 0
                 "2","2__Confirmar","0__Cancelar",                                                                                        // Layer 1
                 "4","3__Tamano jeringa","4__Marca jeringa","5__Selec. volumen","0__Volver ",                                             // Layer 2
                 "4","0__Dosis de 50mL","0__Dosis de 20mL","0__Dosis de 10mL","0__Dosis de 05mL",                                         // Layer 3
                 "6","0__BD Plastipak","0__Fresenius Inject","0__Braun Omnifix","0__Braun Perfusor", "0__PIC Indolor", "0__Terumo",       // Layer 4
                 "2","4__Español","4__Inglés"};                                                                                           // Layer 5

// VALUES ARRAY
// TYPES, 1 numeric / 2 character value range
// 1 - type,value,increments,min,max
// 2 - type,starting value in options array,lowest value options array,max value options array
int values[] = {
                1,11,25,50,1450, //0-4 WATCH1
                2,2,0,2,         //5-8
                1,600,25,75,600, //9-13
                
                1,11,25,50,1450, //14-18 WATCH2
                2,2,0,2,         //19-22
                1,600,25,75,600, //23-27
                
                1,11,25,50,1450, //28-32 WATCH3
                2,2,0,2,         //33-36
                1,600,25,75,600, //37-41
                 
                1,11,25,50,1450, //42-46 WATCH4
                2,2,0,2,         //47-50
                1,600,25,75,600, //51-55
                
                2,4,3,4,         //56-59 WATCH1 ACTIVE
                2,4,3,4,         //60-63 WATCH2 ACTIVE
                2,4,3,4,         //64-67 WATCH3 ACTIVE
                2,4,3,4};        //68-71 WATCH4 ACTIVE
                
                
String options[] = {"CW","CCW","MIX",
                    "No","Sí"};                 

// Custom character for LCD.

byte cursor[8] = {
  0b00000,
  0b10000,
  0b01000,
  0b00111,
  0b01000,
  0b10000,
  0b00000,
  0b00000
};

byte watch[8] = {
  0b01110,
  0b01110,
  0b11011,
  0b10001,
  0b10001,
  0b11011,
  0b01110,
  0b01110
};

byte cursor[8] = {
  0b00100,
  0b00100,
  0b01110,
  0b01110,
  0b01110,
  0b01110,
  0b00100,
  0b01110
};

int currentType = 0;
int value = 0;
int numIncr = 0;
int Min = 0;
int Max = 0;

int currentLayer = 0;
int lastLayer = 99;
int currentLength = menu[0].toInt();
int currentPosition = 0;
int currentSelect = 1;
int currentChange = 0;
String currentPress = "";
float currentlcdLayerFloat = 0;
int currentlcdLayer = 0;
int lastlcdLayer = 0;
int lcdUpdated = 0;
int currentLine = 0;
int cursorLayer = 0;
int cursorPosition = 0;
int valueLength = 0;

void setup() {
  Serial.begin(9600);

  // Map rotary button to actions single and doubleclick.
  button0.attachClick(singleClick);
  button0.attachDoubleClick(doubleClick);

  lcd.begin (16,2);
  lcd.setBacklightPin(3,POSITIVE);
  lcd.setBacklight(HIGH);
  lcd.home();

  // Create the custom character.
  lcd.createChar(0, cursor);
  lcd.createChar(1, watch);

  lcd.setCursor (0,0);  
  lcd.print(" Perfusor ECMO");
  delay(2000);
  clearLine(0);

  // Set the select cursor on the first line.
  cursorLayer = 0;
  lcd.setCursor (0,cursorLayer);  
  writeCursor();

}

void loop() {
    
    // Listen to button presses.
    button0.tick();

    // Listen if the rotary encoder moves.
    rotary_check();
    
    // Print the LCD menu.
    lcdMenu();

}

void singleClick() {

  // IF current layer number is the same as redirect layer number, we stay on the same layer
  // AND no item is selected in the menu
  // AND the selected item has a redirect to another layer
  if(currentLayer == menu[currentPosition + currentSelect].substring(0,1).toInt() && menu[currentPosition + currentSelect].substring(1,3) != "__" && currentPress == ""){
    
    currentPress = menu[currentPosition + currentSelect].substring(3);
    currentChange = menu[currentPosition + currentSelect].substring(1,3).toInt();
    
    Serial.println("Currentpress: " + currentPress);
    
    currentType = values[currentChange];
    value = values[currentChange + 1];

    // Type select change is numeric
    if(currentType == 1){
      Min = values[currentChange + 3];
      Max = values[currentChange + 4];
      numIncr = values[currentChange + 2];
      
      Serial.println("Currentvalue: " + String(value));
      Serial.println("Increments: " + String(numIncr));
      Serial.println("Min: " + String(Min));
      Serial.println("Max: " + String(Max));

      
      valueLength = String(value).length();
      
    // Type select change is character range
    } else if(currentType == 2){
      Min = values[currentChange + 2];
      Max = values[currentChange + 3];

      Serial.println("Currentvalue: " + options[value]);
      Serial.println("Options: ");
      
      for (int i=Min; i <= Max; i++){
        Serial.println(options[i]);
      }

      valueLength = options[value].length();

    }

    clearSelect();
    cursorPosition = 15 - valueLength;
    lcd.setCursor(cursorPosition,cursorLayer);
    writeCursor();

  // ELSE IF something is selected in the menu, and the button is pressed again. We deselect the item.  
  } else if(currentPress != ""){
    
    currentValues();
    currentPress = "";
    currentChange = 0;

    clearChar(cursorPosition,cursorLayer);
    lcd.setCursor(0,cursorLayer);
    writeCursor();
    
  // IF nothing is selected and nothing will be deselected, move to the redirect layer listed in the first position of the array.  
  } else {
    
    currentLayer = menu[currentPosition + currentSelect].substring(0,1).toInt();
    currentSelect = 1;
    currentlcdLayerFloat = 0;
    currentlcdLayer = 0;
    lastlcdLayer = 0;

    clearSelect();
    cursorLayer = 0;
    lcd.setCursor (0,cursorLayer);  
    writeCursor();
    
  }
  
}

// Reset to layer 0.
void doubleClick() {
  if(currentLayer == 0){
    currentLayer = 0;
    currentSelect = 1;
    currentlcdLayerFloat = 0;
    currentlcdLayer = 0;
    lastlcdLayer = 0;
  
    clearSelect();
    cursorLayer = 0;
    
    lcd.clear();
    lcdUpdated = 0;
  }
  if(currentLayer != 0){
    currentLayer = 0;
    currentSelect = 1;
    currentlcdLayerFloat = 0;
    currentlcdLayer = 0;
    lastlcdLayer = 0;
  
    clearSelect();
    cursorLayer = 0;
    lcd.setCursor (0,cursorLayer);  
    writeCursor();
  }
}

void rotary_check(){

  // Constantly read the position of the rotary encoder
  long newPosition = myEnc.read() / 4;

  // IF the new position of the encoder is different then the old position
  if (newPosition != oldPosition) {
       
    // IF nothing has been selected in the menu
    if(currentPress == ""){

      if(newPosition > oldPosition && currentSelect < currentLength){
        clearSelect();
        currentSelect++;
        currentlcdLayerFloat = currentlcdLayerFloat + 0.5;
        currentlcdLayer = currentlcdLayerFloat;

        cursorSelect();
        
        lcd.setCursor (0,cursorLayer);  
        writeCursor();
        Serial.println("> " + menu[currentPosition + currentSelect].substring(3));

      } else if (newPosition < oldPosition && currentSelect != 1){
        clearSelect();
        currentSelect--;
        currentlcdLayerFloat = currentlcdLayerFloat - 0.5;
        currentlcdLayer = currentlcdLayerFloat;

        cursorSelect();

        lcd.setCursor (0,cursorLayer);  
        writeCursor();
        Serial.println("> " + menu[currentPosition + currentSelect].substring(3));
  
      }
      
      if(lastlcdLayer != currentlcdLayer){
        lcdUpdated = 0;
      }
      
      lastlcdLayer = currentlcdLayer;      
      oldPosition = newPosition;



    // IF something has been selected in the menu, we are going to change the value of a menu item.
    } else if(currentPress != ""){

      
      lcd.setCursor(cursorPosition + 1,cursorLayer);
      // IF the new position is HIGHER then the old position
      if(newPosition > oldPosition){
        clearChar(cursorPosition,cursorLayer);
        
        // IF the selected item has a change type that is NUMERIC.
        // AND the MAXIMUM of the selected item has not been reached. 
        // We change the value UPWARDS with the icrements listed in the array.
        // SAME applies for next ELSE IF, just for the change type character. And the next ELSE IF we just go down.
        if(currentType == 1 && value < Max){
            value = value + numIncr;
            values[currentChange + 1] = value;
            Serial.println(value);

            clearValue();
            valueLength = String(value).length();
            cursorPosition = 15 - valueLength;
            lcd.setCursor(cursorPosition + 1,cursorLayer);
            lcd.print(value);
          }

        if(currentType == 2 && value < Max){
            value++;
            values[currentChange + 1] = value;
            Serial.println(options[value]);

            clearValue();
            valueLength = options[value].length();
            cursorPosition = 15 - valueLength;
            lcd.setCursor(cursorPosition + 1,cursorLayer);
            lcd.print(options[value]);
          }
          lcd.setCursor(cursorPosition,cursorLayer);
          writeCursor();
        
      } else {
        clearChar(cursorPosition,cursorLayer);
        
        if(currentType == 1 && value > Min){
          value = value - numIncr;
          values[currentChange + 1] = value;
          Serial.println(value);

          clearValue();
          valueLength = String(value).length();
          cursorPosition = 15 - valueLength;
          lcd.setCursor(cursorPosition + 1,cursorLayer);
          lcd.print(value);
        }

        if(currentType == 2 && value > Min){
            value--;
            values[currentChange + 1] = value;
            Serial.println(options[value]);

            clearValue();
            valueLength = options[value].length();
            cursorPosition = 15 - valueLength;
            lcd.setCursor(cursorPosition + 1,cursorLayer);
            lcd.print(options[value]);
          }
          lcd.setCursor(cursorPosition,cursorLayer);
          writeCursor();
        
      }

      
        
      oldPosition = newPosition;
    } else {
      oldPosition = newPosition;
    }
    
    
    
  }
}
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

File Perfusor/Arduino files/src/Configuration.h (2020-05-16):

/**
 * @file Configuration.h
 * @author Limako
 * @author Sergio Gasquez Arcos (sergio.gasquez@gmail.com)
 * @brief Connections and definitions for the system 
 * @version 0.1
 * @date 2020-05-03
 * 
 * @copyright Copyright (c) 2020
 * 
 */

#ifndef CONFIGURATION_H
#define CONFIGURATION_H

// Display Configuration
#define LCD_COLS 16
#define LCD_ROWS 2
#define LCD_I2C_ADDRESS 0x27

// Syringe Configuration
#define SLIDER_LENGTH 82      // Slider length in mm
#define STEPS_PER_TURN 3200   // Number of steps per turn
#define MOVE_PER_TURN 2       // Advance per turn in mm

// Choose Driver
#define NEMA17
// #define BYJ


#ifdef BJY
#define STEPPER_PIN_1 2
#define STEPPER_PIN_2 3
#define STEPPER_PIN_3 4
#define STEPPER_PIN_4 5
#define STEPPER_FORWARD_BUTTON_PIN 6
#define STEPPER_BACKWARD_BUTTON_PIN 7
#define ACCEPT_BUTTON_PIN 8
#define END_STOP_PIN 9
#define POTENTIOMETER_PIN A0
#endif   // BJY

#ifdef NEMA17
#define ENCODER_PIN 3
#define STEPPER_STEP_PIN 5
#define STEPPER_DIR_PIN 2
#define ENABLE_PIN 8
#define STEPPER_FORWARD_BUTTON_PIN 9
#define STEPPER_BACKWARD_BUTTON_PIN 10
#define ACCEPT_BUTTON_PIN 11
#define END_STOP_PIN 12
#define POTENTIOMETER_PIN A0
#endif   // NEMA17

#endif   // CONFIGURATION_H

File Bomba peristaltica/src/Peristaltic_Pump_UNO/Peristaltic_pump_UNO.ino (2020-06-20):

/*
 
  Author: Francisco Ochando

  Description: Peristalthic Pump, LCD and buttons. Current sensor.
  
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
  See <http://www.gnu.org/licenses/>.

*/

/*
Peristaltic Pump:
Commands:
move <speed> Set continuous pump rotation speed (rpm)
*/

#include <AccelStepper.h>
#include <FlexyStepper.h>
#include "Peristaltic_pump.h"
#include "Sensor.h"
#include "Pump.h"
#include <TimerOne.h>

Peristaltic BOMBA;
//AccelStepper Motor(1, PIN_STEP, PIN_DIR);
FlexyStepper stepper;
Pump MOTOR;
Sensor sensor;

byte ledstate = LOW; // Blinking indicator LED

String buffer;
byte readout;

long last_time = 0;
long steps = 0;
uint16_t stepper_timer = 0;
uint16_t step_time = 0;
uint16_t update_timer = 0;
uint16_t speed_motor = 0;
uint16_t Rpm = 0;
uint16_t Rpm_old = 0;
uint16_t stepcount = 0;
uint16_t counter = 0;
unsigned long time;
bool ena = false;             // Bomba activada
bool fwd = true;              // Direccion (true = dcha)
bool alarm = false;



void InitStepper() 
{ 

  stepper.connectToPins(PIN_STEP, PIN_DIR);
  stepper.setStepsPerRevolution( 400 );
  stepper.setTargetPositionInSteps( 8000 );
  stepper.setSpeedInRevolutionsPerSecond( Rpm/60 );
  stepper.setAccelerationInRevolutionsPerSecondPerSecond( Rpm/60 );
  stepper.setTargetPositionInRevolutions( Rpm*60 ); // Target en RPM = 1 hora de giro

}
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

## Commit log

2020-04-28 Vídeo de Ramsés en Zoom
2020-04-28 * para los prototipos
2020-04-28 Guía de jeringuillas
2020-05-01 Update Papers/Oxygenator Design/fisher2003.pdf, Papers/Oxygenator Design/F1.ppt, Papers/Oxygenator Design/nearinfrared-blood-flow-and-oxygenation-measurement-in-deep-tiss.pdf, Papers/Oxygenator Desig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
2020-05-02 Colocar STLs
    [Caja.stl, Caja8mm.stl, Rotor.stl, Rotor8mm.stl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]
2020-05-03 Fix folder name
    [Caja.stl, Caja8mm.stl, Rotor.stl, Rotor8mm.stl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]
2020-05-03 Arduino_LCD test
2020-05-04 Replace Rotor.stl
    [Rotor.stl]
2020-05-07 Replace SyringeDriver.cpp
2020-05-07 Add the feature of taking input parameters of flow and load.It now displays the remaining load on the display and also computes the progress
2020-05-11 Add stl files
    [Part Studio 1.stl, Part Studio 2.stl, Part Studio 3.stl, Part Studio 4.stl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]
2020-05-11 Upload New File
    [Perfusor_Plastikete.stl]
2020-05-13 Replace SyringeDriver.h
2020-05-17 Pump states update
2020-05-17 Bomba peristáltica LEGO
    [Frontal (x4).stl, Lateral (x2).stl, Rodillo inferior.stl, Rodillo superior.stl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]
2020-06-13 Update Peristaltic_pump_UNO.ino. Revisada la lectura de botones dssde el bucle principal.
2020-06-13 Update Pump.cpp. Modificada la función setDir() para el pin de cambio de dirección.
2020-06-13 Normativa de fabricacion para poder homologar.
2020-06-13 Proposicion de diagranma de flujo para el funcionamiento de la bomba perfusora.
2020-06-13 STL que faltaban
    [Part Studio 10.stl, Part Studio 11.stl, Part Studio 12.stl, Part Studio 13.stl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]
2020-06-14 Diagrama de bloques extraído de la idea. Se puede mejorar.
2020-06-14 update stl files
    [Part Studio 10.stl, Part Studio 11.stl, Part Studio 12.stl, Part Studio 13.stl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]
2020-06-14 remove stl files
    [Part Studio 10.stl, Part Studio 11.stl, Part Studio 12.stl, Part Studio 13.stl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]
2020-06-18 Upload New File Máquina de estados
2020-06-20 Update Peristaltic_pump_UNO.ino (Funcion de potenciómetro y stepper)
2020-06-20 Update Hid.cpp (mejora de selección de RPMs con potenciómetro y pulsadores)
2020-06-20 Update Pump.cpp (setters y función getRPS para velocidad stepper)
2020-06-21 Upload New File HB100 sensor radar doppler 10GHz

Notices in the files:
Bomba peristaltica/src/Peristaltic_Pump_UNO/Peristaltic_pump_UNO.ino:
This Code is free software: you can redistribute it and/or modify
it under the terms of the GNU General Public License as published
